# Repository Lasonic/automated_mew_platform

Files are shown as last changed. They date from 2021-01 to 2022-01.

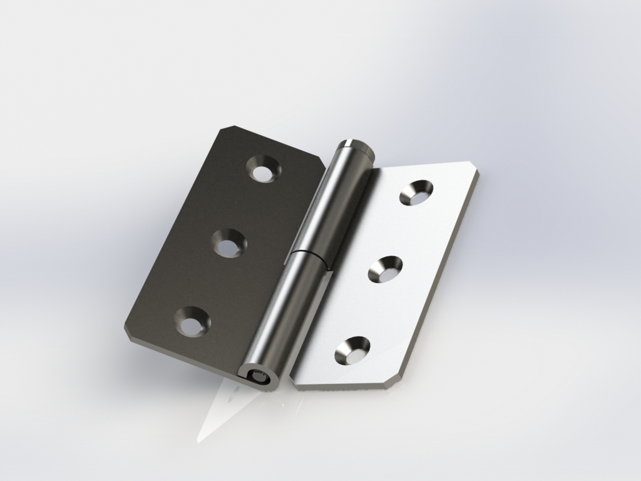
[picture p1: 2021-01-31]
CAD/Hinges/prt.JPG

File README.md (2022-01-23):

# automated_mew_platform
Files including all python, arduino and matlab code necessary to run the platform.  

Repository withe design files and code for Automated MEW platform with real-time process monitoring.

Publication avalilabe at :https://www.sciencedirect.com/science/article/pii/S2468067221000766

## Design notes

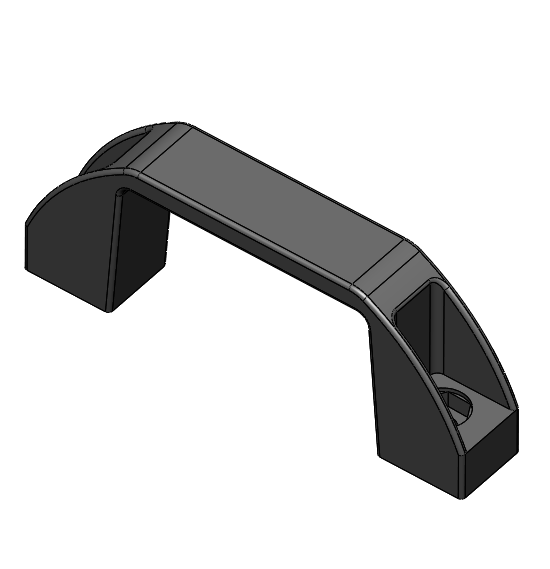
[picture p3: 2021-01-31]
CAD/Handle/Capture.PNG

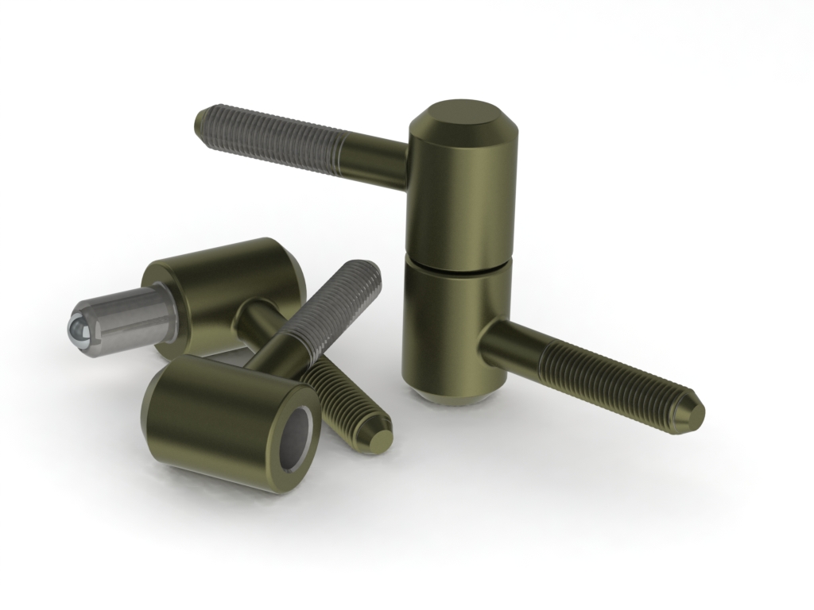
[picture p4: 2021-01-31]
CAD/Hinges/trt3.JPG

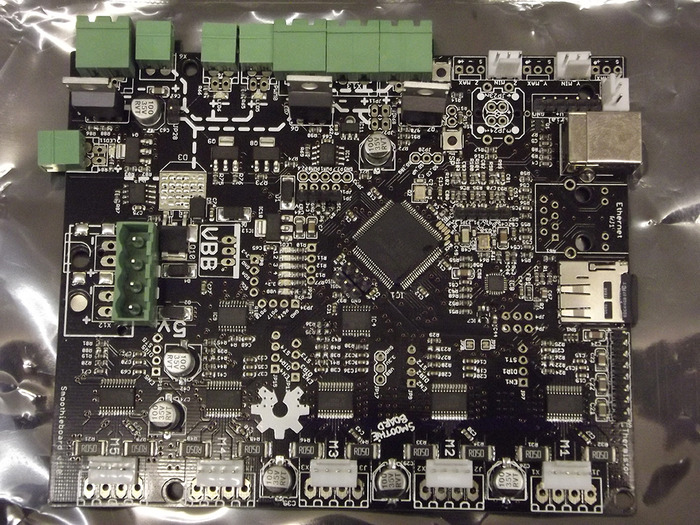
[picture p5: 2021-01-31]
CAD/Smoothie board/Renderings/4c55661e1bbb966e016c8f90354837cf_large.jpg

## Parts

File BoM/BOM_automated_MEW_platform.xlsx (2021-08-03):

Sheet: Mechanical
Componenet | Source | Catalog number | Quantity | Cost/Unit (USD) | Total cost (USD) | Qty | Part Name | Part Link | Comments
Framework |  |  |  |  |  | 1 | OpenBuilds MiniMill | http://openbuildspartstore.com/openbuilds-minimill/ | Convenient One Click Bundle
Profile 30 x 30 mm (slot 8 mm) | GAP Engineering Pty Ltd (Australia) | 084.107.002 needs cutting | 19.464 | 11.04 | 214.88 | 8 | 8mm Shim | http://openbuildspartstore.com/8mm-shim/ | SKU 835
Profile 20 x 20 mm (slot 6 mm) | GAP Engineering Pty Ltd (Australia) | 084.111.001 needs cutting | 2.21 | 7.71 | 17.04 | 6 | 90 Degree Joining Plate | http://openbuildspartstore.com/90-degree-joining-plate/ | SKU 610
Profile 20 x80 mm (V slot) | Makerstore(Australia) | LR-2080-S needs cutting | 2 | 22.82 | 45.64 | 6 | Aluminum Spacers - 3mm | http://openbuildspartstore.com/aluminum-spacers/ | SKU 175
Clamping angle 29x29mm | GAP Engineering Pty Ltd (Australia) | 084.305.010 | 50 | 2.16 | 108.00 | 6 | Aluminum Spacers - 40mm | http://openbuildspartstore.com/aluminum-spacers/ | SKU 95
Clamping angle 18x18mm | GAP Engineering Pty Ltd (Australia) | 084.305.032 | 40 | 1.66 | 66.40 | 8 | Aluminum Spacers - 6mm | http://openbuildspartstore.com/aluminum-spacers/ | SKU 90
Hammer Nut M5 slot 8 | GAP Engineering Pty Ltd (Australia) | 084.302.023 pack of 5 | 20 | 3.08 | 61.60 | 3 | Anti-Backlash Nut Block | http://openbuildspartstore.com/anti-backlash-nut-block-fo... | SKU 1055
Hammer Nut M5 slot 6 | GAP Engineering Pty Ltd (Australia) | 084.302.061 pack of 5 | 20 | 3.08 | 61.60 | 6 | Ball Bearing 688Z 8x16x5 | http://openbuildspartstore.com/ball-bearing-688z-8x16x5/ | SKU 780
Nut M5 | GAP Engineering Pty Ltd (Australia) | 084.302.002 pack of 25 | 2 | 3.85 | 7.70
Nut M8 | GAP Engineering Pty Ltd (Australia) | 084.302.002 pack of 25 | 2 | 3.85 | 7.70 | 6 | Black Angle Corner Connector | http://openbuildspartstore.com/black-angle-corner-connector/ | SKU 540
Stainless steel plain washer M5 | RS componenets (Australia) | 527-397 | 1 | 9.84 | 9.84 | 10 | Cable Ties | http://openbuildspartstore.com/cable-ties-10-pack/ | SKU 675 - Sold in Packs - Need 10 Singles
Screw M8x20 | GAP Engineering Pty Ltd (Australia) | 084.301.003 pack of 25 | 2 | 4.62 | 9.24 | 10 | Cast Corner Bracket | http://openbuildspartstore.com/cast-corner-bracket/ | SKU 490
Screw M5x20 | GAP Engineering Pty Ltd (Australia) | 084.301.036 pack of 25 | 2 | 2.89 | 5.78 | 5 | C-Beam® Linear Rail | http://openbuildspartstore.com/c-beam-linear-rail/ | (1) 107mm (3) 250mm (1) 390mm
Low profile M5x15 | Makerstore(Australia) | SCREWS-M5-LP-15/10 pack of 10 | 10 | 1.38 | 13.80
Door handle | GAP Engineering Pty Ltd (Australia) | 084.504.002 | 3 | 3.39 | 10.17 | 1 | C-Beam® Gantry Plate - Double Wide | http://openbuildspartstore.com/c-beam-gantry-plate-double... | SKU 2026
Aluminium hinge | GAP Engineering Pty Ltd (Australia) | 084.500.003 | 6 | 11.93 | 71.58 | 6 | C-Beam® End Mount | http://openbuildspartstore.com/c-beam-end-mount/ | SKU 965
Alumimium sheet 770x290x3mm | Action Alumimium (Australia) | N/A | 1 | 15.26 | 15.26
Enclosure
Acrylic sheet, 4.5mm, matt black | Mulford Plastics Pty Ltd (Australia) | ACB4.5_11440 | 3 | 125.38 | 376.14
Low profile M5x15 | Makerstore(Australia) |  |  |  | 0.00
Hammer Nut M5 slot 8 | GAP Engineering Pty Ltd (Australia) |  |  |  | 0.00
Printhead |  |  |  |  |  | 8 | Eccentric Spacer - 6mm | http://openbuildspartstore.com/eccentric-spacer/ | SKU 226
Teflon main body | Eastagate engineering (Australia) | Quotation based on the provided drawings | 1 | 85.55 | 85.55
Teflon cap | Eastagate engineering (Australia) | Quotation based on the provided drawings | 1 | 36.22 | 36.22
Teflon small insert | Eastagate engineering (Australia) | Quotation based on the provided drawings | 1 | 15.1 | 15.10
Brass insert | Eastagate engineering (Australia) | Quotation based on the provided drawings | 1 | 63.6 | 63.60
 |  |  |  |  | 0.00
Linear stages |  |  |  |  |  | 2 | V-Slot® Door Handle | http://openbuildspartstore.com/v-slot-door-handle/ | SKU 556
OpenBuilds MiniMill CNC Machine | Openbuilds(USA) | 2170-Bundle | 1 | 549.99 | 549.99 | 2 | Jog Knob | http://openbuildspartstore.com/jog-knob/ | SKU 2040
This includes:
8mm Shim | Openbuilds(USA) | SKU 835 | 8 |  |  | 1 | L Bracket - Single | http://openbuildspartstore.com/l-bracket/ | SKU 545
90 Degree Joining Plate | Openbuilds(USA) | SKU 610 | 6 |  |  | 3 | Lead Screw | http://openbuildspartstore.com/8mm-metric-acme-lead-screw/ | (1) 290mm (1) 315mm (1) 455mm
Aluminum Spacers - 3mm | Openbuilds(USA) | SKU 175 | 6 |  |  | 6 | Lock Collar - 8mm | http://openbuildspartstore.com/lock-collar/ | SKU 840
Aluminum Spacers - 40mm | Openbuilds(USA) | SKU 95 | 6 |  |  | 48 | Low Profile Screws M5 - 10mm | http://openbuildspartstore.com/low-profile-screws-m5/ | SKU 878 - Sold in Packs - Need 42 Singles
Aluminum Spacers - 6mm | Openbuilds(USA) | SKU 90 | 8 |  |  | 8 | Low Profile Screws M5 - 12mm | http://openbuildspartstore.com/low-profile-screws-m5/ | SKU 2190 - Sold in Packs - Need 8 Singles
Anti-Backlash Nut Block | Openbuilds(USA) | SKU 1055 | 3 |  |  | 30 | Low Profile Screws M5 - 20mm | http://openbuildspartstore.com/low-profile-screws-m5/ | SKU 750 - Sold in Packs - Need 30 Singles
Ball Bearing 688Z 8x16x5 | Openbuilds(USA) | SKU 780 | 6 |  |  | 8 | Low Profile Screws M5 - 25mm | http://openbuildspartstore.com/low-profile-screws-m5/ | SKU 20 - Sold in Packs - Need 8 Singles
Black Angle Corner Connector | Openbuilds(USA) | SKU 540 | 6 |  |  | 6 | Low Profile Screws M5 - 55mm | http://openbuildspartstore.com/low-profile-screws-m5/ | SKU 760 - Sold in Packs - Need 6 Singles
Cable Ties | Openbuilds(USA) | SKU 675 - Sold in Packs - Need 10 Singles | 10 |  |  | 21 | Low Profile Screws M5 - 8mm | http://openbuildspartstore.com/low-profile-screws-m5/ | SKU 946 - Sold in Packs - Need 21 Singles
Cast Corner Bracket | Openbuilds(USA) | SKU 490 | 10 |  |  | 8 | Xtreme Mini V Wheel™ Kit | http://openbuildspartstore.com/xtreme-mini-v-wheel-kit/ | SKU 876
C-Beam® Linear Rail | Openbuilds(USA) | (1) 107mm (3) 250mm (1) 390mm | 5 |  |  | 4 | Precision Shim - 10x5x1mm | http://openbuildspartstore.com/precision-shim-10x5x1mm/ | SKU 05
C-Beam® Gantry Plate - Double Wide | Openbuilds(USA) | SKU 2026 | 1 |  |  | 1 | Router/Spindle Mount | http://openbuildspartstore.com/router-spindle-mount/ | SKU 990
C-Beam® End Mount | Openbuilds(USA) | SKU 965 | 6 |  |  | 10 | Self Tapping Screw | http://openbuildspartstore.com/self-tapping-screw/ | SKU 720
C-Beam® Gantry Plate - XLarge | Openbuilds(USA) | SKU 2030 | 2 |  |  | 60 | Tee Nuts - M5 | http://openbuildspartstore.com/tee-nuts-25-pack/ | SKU 536 - Sold in Packs - Need 60 Singles
Drop In Tee Nuts | Openbuilds(USA) | SKU 230 | 4 |  |  | 8 | Xtreme Solid V Wheel™ Kit | http://openbuildspartstore.com/xtreme-solid-v-wheel-kit/ | SKU 465
Eccentric Spacer - 6mm | Openbuilds(USA) | SKU 226 | 8 |  |  | 4 | 3 Hole Joining Strip Plate | http://openbuildspartstore.com/3-hole-joining-strip-plate/ | SKU 646
1/4" x 8mm Flexible Coupling | Openbuilds(USA) | SKU 155 | 3 |  |  | 8 | Low Profile Screws M5 - 27mm | https://openbuildspartstore.com/low-profile-screws-m5-10-... | SKU 2260 - Sold in Packs - Need 8 Singles
V-Slot® Door Handle | Openbuilds(USA) | SKU 556 | 2 |  |  | 1 | Ball Driver Screw Driver Set | https://openbuildspartstore.com/balldriver-screw-driver-set/ | SKU 2145
Jog Knob | Openbuilds(USA) | SKU 2040 | 2 |  |  | 4 | Nylon Insert Hex Locknut M5 - Black | https://openbuildspartstore.com/nylon-insert-hex-locknut-... | SKU 2285
L Bracket - Single | Openbuilds(USA) | SKU 545 | 1 |  |  | 1 | OpenBuilds 8mm Spanner Wrench | https://openbuildspartstore.com/openbuilds-8mm-spanner-wr... | SKU 2265
Lead Screw | Openbuilds(USA) | (1) 290mm (1) 315mm (1) 455mm | 3 |  |  | 6 | Round Head Cutting Screws | https://openbuildspartstore.com/round-head-cutting-screws... | SKU 2440
Lock Collar - 8mm | Openbuilds(USA) | SKU 840 | 6 |  |  | 1 | Spindle/Router LED Light Ring | https://openbuildspartstore.com/spindle-router-led-light-... | SKU 2225
Low Profile Screws M5 - 10mm | Openbuilds(USA) | SKU 878 - Sold in Packs - Need 42 Singles | 48 |  |  | 1 | Xtension Wire 2C - 3' | https://openbuildspartstore.com/xtension-wire-by-the-foot/ | SKU 2545-By-the-Foot
Low Profile Screws M5 - 12mm | Openbuilds(USA) | SKU 2190 - Sold in Packs - Need 8 Singles | 8 |  |  | 3 | Xtension Wire 4C - 3' | https://openbuildspartstore.com/xtension-wire-by-the-foot/ | SKU 2556
Low Profile Screws M5 - 20mm | Openbuilds(USA) | SKU 750 - Sold in Packs - Need 30 Singles | 30 |  |  | 1 | Rubber Feet Set | https://openbuildspartstore.com/rubber-feet-set-4-pack/ | SKU 2645-Set
Low Profile Screws M5 - 25mm | Openbuilds(USA) | SKU 20 - Sold in Packs - Need 8 Singles | 8 |  |  | 1 | Flexible Tubing - 1' | https://openbuildspartstore.com/flexible-corrugated-tubing/ | SKU 2675-By-the-Foot
Low Profile Screws M5 - 55mm | Openbuilds(USA) | SKU 760 - Sold in Packs - Need 6 Singles | 6 |  |  | 1 | Flexible Tubing - 1.5' | https://openbuildspartstore.com/flexible-corrugated-tubing/ | SKU 2675-By-the-Foot
Low Profile Screws M5 - 8mm | Openbuilds(USA) | SKU 946 - Sold in Packs - Need 21 Singles | 21 |  |  | 4 | Flexible Tubing Clamps | https://openbuildspartstore.com/flexible-tubing-clamps/ | SKU 2685
Xtreme Mini V Wheel™ Kit | Openbuilds(USA) | SKU 876 | 8 |  |  | 3 | Xtension Limit Switch Kit | https://openbuildspartstore.com/xtension-limit-switch-kit/ | SKU 2805
Precision Shim - 10x5x1mm | Openbuilds(USA) | SKU 05 | 4 |  |  | 3 | Xtension Wire 3C - 3' | https://openbuildspartstore.com/xtension-wire-by-the-foot/ | SKU 2905
Router/Spindle Mount | Openbuilds(USA) | SKU 990 | 1 |  |  | 2 | Slot Cover/Panel Holder - 250mm - Black | https://openbuildspartstore.com/slot-cover-panel-holder/ | SKU 125-LP-B
Self Tapping Screw | Openbuilds(USA) | SKU 720 | 10 |  |  | 4 | NEMA 23 Stepper Motor | https://openbuildspartstore.com/nema-23-stepper-motor/ | SKU 518 - Option to Include With Bundle
Tee Nuts - M5 | Openbuilds(USA) | SKU 536 - Sold in Packs - Need 60 Singles | 60 |  |  | 1 | 24V Meanwell Power Supply Bundle | https://openbuildspartstore.com/24v-meanwell-power-supply... | SKU 591 - Option to Include With Bundle
Xtreme Solid V Wheel™ Kit | Openbuilds(USA) | SKU 465 | 8 |  |  | 1 | Dust Shoe | https://openbuildspartstore.com/dust-shoe/ | SKU 2795 - Option to Include With Bundle
3 Hole Joining Strip Plate | Openbuilds(USA) | SKU 646 | 4 |  |  | 1 | BlackBox Motion Control System | https://openbuildspartstore.com/blackbox-motion-control-s... | SKU 2790 - Option to Include With Bundle
Low Profile Screws M5 - 27mm | Openbuilds(USA) | SKU 2260 - Sold in Packs - Need 8 Singles | 8 |  |  | 1 | DeWALT DWP611 Compact Router | https://openbuildspartstore.com/dewalt-dwp611-compact-rou... | SKU 2390 - Option to Include With Bundle
Ball Driver Screw Driver Set | Openbuilds(USA) | SKU 2145 | 1 |  |  | 1 | VCarve Desktop | https://openbuildspartstore.com/vcarve-desktop/ | SKU 2885 - Option to Include With Bundle
Nylon Insert Hex Locknut M5 - Black | Openbuilds(USA) | SKU 2285 | 4 |  |  | 0
OpenBuilds 8mm Spanner Wrench | Openbuilds(USA) | SKU 2265 | 1
Round Head Cutting Screws | Openbuilds(USA) | SKU 2440 | 6
Spindle/Router LED Light Ring | Openbuilds(USA) | SKU 2225 | 1
Xtension Wire 2C - 3' | Openbuilds(USA) | SKU 2545-By-the-Foot | 1
Xtension Wire 4C - 3' | Openbuilds(USA) | SKU 2556 | 3
Rubber Feet Set | Openbuilds(USA) | SKU 2645-Set | 1
Flexible Tubing - 1' | Openbuilds(USA) | SKU 2675-By-the-Foot | 1
Flexible Tubing - 1.5' | Openbuilds(USA) | SKU 2675-By-the-Foot | 1
Flexible Tubing Clamps | Openbuilds(USA) | SKU 2685 | 4
Xtension Limit Switch Kit | Openbuilds(USA) | SKU 2805 | 3
Xtension Wire 3C - 3' | Openbuilds(USA) | SKU 2905 | 3
Slot Cover/Panel Holder - 250mm - Black | Openbuilds(USA) | SKU 125-LP-B | 2
Printbed
Aluminium plate 120x120x10mm | Action Alumimium (Australia) | N/A | 1 | 7.7 | 7.70
Low Profile Screws M5 - ? | Makerstore(Australia) |  |  |  | 0.00
 |  |  |  |  | 1860.53

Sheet: Electrical
Component | Source | Catalog number | Quantity | Cost/Unit (USD) | Total cost (USD)
Embedded control unit
Smoothieboard 5XC v1.1 | Uberlock (USA) | smoothie_5x | 1 | 188.97 | 188.97
Arduino Due | RS Components (Australia) | 769-7412 | 1 | 40.76 | 40.76
USB to TTL Serial Cable | Core Electronics(Australia) | ADA954 | 2 | 17.18 | 34.36
PCB components
PCB manufacture | JLCPCB | N/A | 1 | 7.41 | 7.41
Resistor network 10K/10K | Mouser electronics | 71-MPM2002AT1 | 2 | 4.74 | 9.48
Resistor network 10K/5K | Mouser electronics | 71-MPMA50011002AT5 | 2 | 4.48 | 8.96
Capacitor ceramic 100V 0.10uF 5% | Mouser electronics | 810-FA26C0G2A104JRU6 | 5 | 1.18 | 5.9
Capacitor Aluminium Electrolytic Radial 800V 100uF | Mouser electronics | 667-EEU-FS1K101L | 2 | 0.81 | 1.62
Operational Amplifier - TLV2371IDR | Mouser electronics | 595-TLV2371IDR | 2 | 1.34 | 2.68
Computing unit
Desktop PC | Dell (Australia) | N/A | 1 | 1148 | 1148
This includes:
RAM: 64GB
CPU: Intel Xeon, W-2125
Operating system: Windows 10, 64-bit
Motion control
Integrated Stepper Servo Motor Nema 23 Closed Loop | Steppernoline (China) | ISS23-10 | 3 | 94.09 | 282.27
Rigid Coupling 8mm-8mm | Steppernoline (China) | ST-RC07 | 3 | 3.03 | 9.09
Process monitoring
Basker Ace ac2440-75um USB3 Mono | Edmund Optics (USA) | #35-927 | 1 | 1542.95 | 1542.95
1.0X 2/3" GoldTL™ Telecentric Lens | Edmund Optics (USA) | #55-350 | 1 | 1667.21 | 1667.21
USB3.1 Locking Cable, 5m | Edmund Optics (USA) | #88-058 | 1 | 40 | 40
Mounting Clamp, 68mm Inner Diameter | Edmund Optics (USA) | #56-024 | 1 | 153.16 | 153.16
Temperature control
Heating element - syringe | Rauschert (Germany) |  | 1 | 192.73 | 192.73
Heating element - ring | Rauschert (Germany) |  |  |  | 0
RS PRO K-type thermocouple | RS Components (Australia) | 804-7915 | 2 | 32.95 | 65.9
RS PRO ANSI thermocouple connector male | RS Components (Australia) | 769-1101 | 2 | 7.53 | 15.06
RS PRO ANSI thermocouple connector female | RS Components (Australia) | 769-1173 | 2 | 3.23 | 6.46
K-type thermocouple wire extension | RS Components (Australia) | 200-0623 - length 25m - need 5m | 0.25 | 39.62 | 9.905
Analog Output K-Type Thermocouple Amplifier | Core Electronics(Australia) | ADA1778 | 2 | 20.81 | 41.62
High voltage
High voltage supply | Gamma High Voltage | RC5-20P/24 | 1 | 557 | 557
High voltage connector |  |  |  |  | 0
Pneumatic pressure system
SMC pressure regulator (ITV1050-31N2L) | SMC Pneumatics (USA) | ITV1050-31N2L | 1 | 294.2 | 294.2
Schmaltz pressure sensor including connecting cable | Schmalz Australia (Australia) | 10.06.02.00561 | 1 | 150 | 150
Input connector |  |  |  |  | 0
output connector |  |  |  |  | 0
Input hose |  |  |  |  | 0
Output hose |  |  |  |  | 0
T junction |  |  |  |  | 0
Power unit
320W 48VDC switching power supply (RSP-320-48) | Mouser electronics | 709-RSP320-48 | 1 | 57.88 | 57.88
350W 12VDC switching power supply (LRS-350-12) | Mouser electronics | 709-LRS350-12 | 1 | 38.28 | 38.28
68W 5VDC & 24VDC dual output switching power supply (RD-65B) | Mouser electronics | 709-RD65B | 1 | 23.49 | 23.49
IEC panel mount connector male | RS Components (Australia) | 352-1803 | 1 | 14.86 | 14.86
2m power cable, IEC to AS/NZS 3112 | RS Components (Australia) | 909-2178 | 1 | 13.01 | 13.01
Flexible 3-core mains cable | Jaycar Electronics (Australia) | WB1562 - sold per meter | 2 | 2.19 | 4.38
DIN rail | RS Components | 467-406 | 1 | 7.63 | 7.63
DIN rail grey terminal | Altronics (Australia) | P2400 | 26 | 2.23 | 57.98
DIN rail green/yellow terminal | Altronics (Australia) | P2412 | 4 | 4.43 | 17.72
Omron 24VDC coil non-latching relay SPDT, 10A | RS Components (Australia) | 329-7178 | 1 | 11.41 | 11.41
DIN rail Omron 5 Pin Relay Socket | RS Components (Australia) | 111-3066 | 1 | 7.58 | 7.58
Black Shorting Link for DIN rail terminals | Altronics (Australia) | P2469 | 2 | 2.87 | 5.74
Red Shorting Link for DIN rail terminals | Altronics (Australia) | P2463 | 2 | 2.87 | 5.74
Safety hardware
Contactless magnetic switch | Element14 (USA) | 2847408 | 2 | 388.26 | 776.52
Wire and connectors
Female Crimp Pins for 0.1" Housings | Core Electronics(Australia) | POLOLU-1930 - pack of 100 | 1 | 6.63 | 6.63
0.1" Crimp Connector Housing: 1x1 | Core Electronics(Australia) | POLOLU-1900 - pack of 25 | 1 | 1.38 | 1.38
0.1" Crimp Connector Housing: 1x4 | Core Electronics(Australia) | POLOLU-1903 - pack of 10 | 1 | 1.38 | 1.38
Power cable 0.5mm^2- RED |  |  |  |  | 0
Power cable 0.5mm^2 - BLACK |  |  |  |  | 0
4 core cable, 0.5mm2, screened | Element14 (USA) | PP001563 - sold per 50 m | 0.2 | 78.39 | 15.68
2 core cable, 0.5mm2, screened | Element14 (USA) | PP001555 - sold per 50m | 0.2 | 50.47 | 10.09
Jumper cable male-female | Core Electronics(Australia) | FIT0365 | 1 | 5.46 | 5.46
Jumper cable male-male | Core Electronics(Australia) | POLOLU-1702 - pack of 50 | 1 | 13.9 | 13.9
Jumper cable female-female | Core Electronics (Australia) | 018-03-DUPONT-PK | 1 | 7.62 | 7.62
Heat shrink kit | Core Electronics (Australia) | PRT-09353 | 1 | 9.13 | 9.13
Drag chain | Makerstore (Australia) | BUN-CDCL | 1 | 65.41 | 65.41
Breadboard | Core Electronics (Australia) | CE00304 | 1 | 5.06 | 5.06
40 Pin Headers | Core Electronics (Australia) | FIT0084 - pack of 10 | 1 | 3.15 | 3.15
 |  |  |  |  | 7662.807

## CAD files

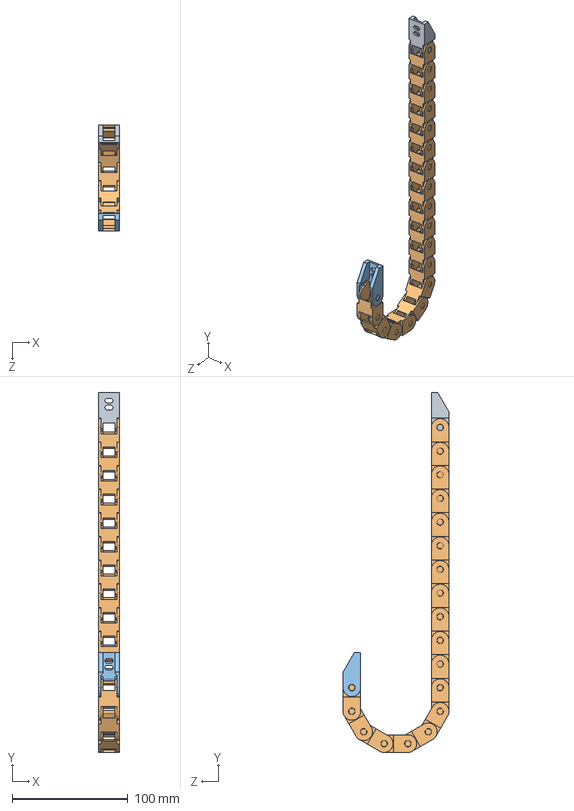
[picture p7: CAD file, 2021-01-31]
CAD/Drag chain/Drag Chain 10x10.SLDASM
17.8 x 310.8 x 91.5 mm
Bloc 06.stp
Bloc 04.stp x 18
Bloc 05.stp

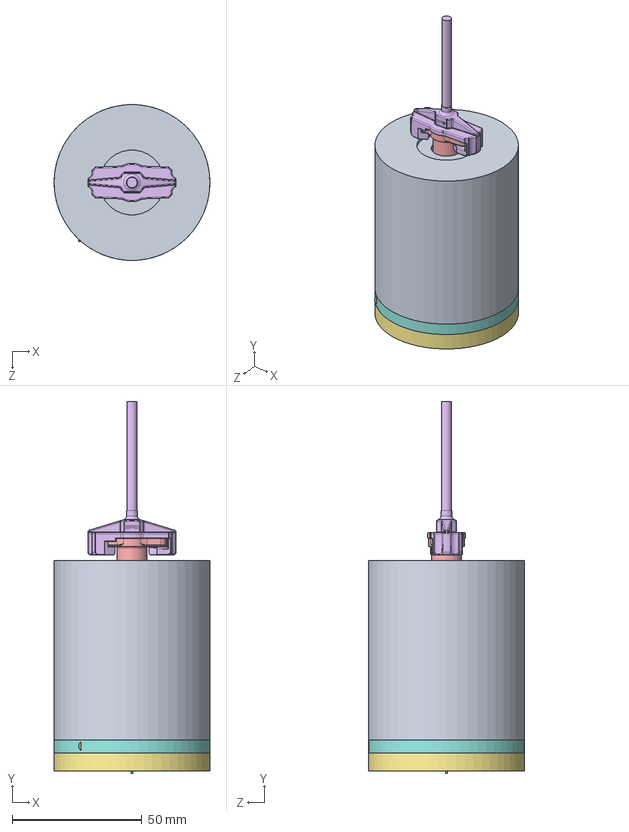
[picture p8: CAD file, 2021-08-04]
CAD/Printhead/Printhead CAD/head_1111.SLDASM
60.0 x 143.2 x 60.0 mm
Ceramic heater_CSIRO
heater_bottom_CSIRO
23GP_final
NORDSONEFD-7012030 PISTON O 3CC WH WIPER
NORDSONEFD-7012013 BARREL O 3CC CL
PumpConnection_CSIRO
ring_bottom
ring_middle
TUBE_TOP
brass

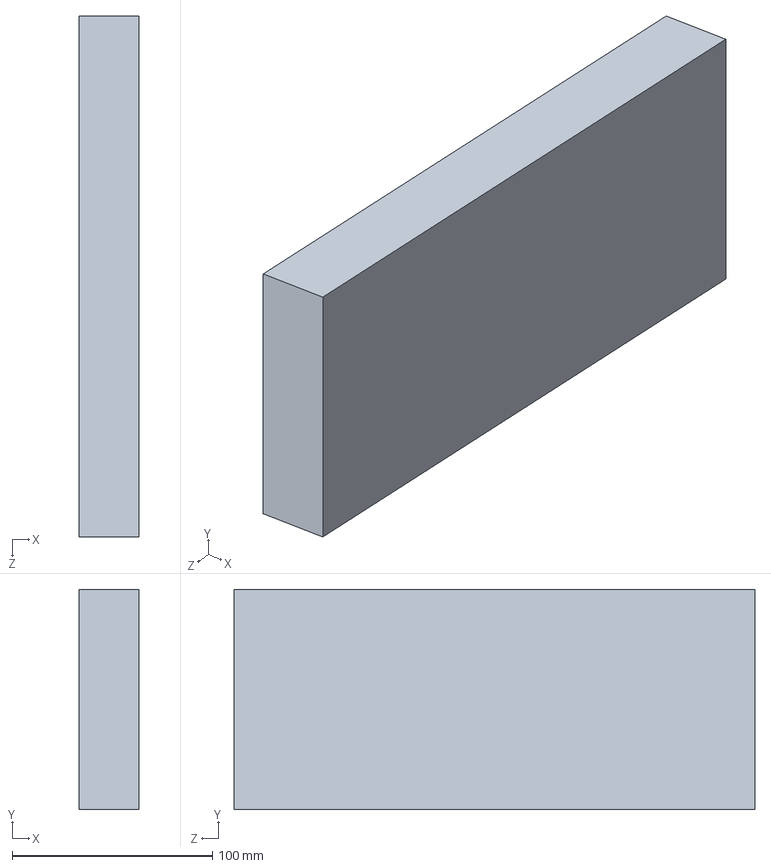
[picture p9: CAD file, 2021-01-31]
CAD/Electrical components/24VDC PSU + mains adapter.SLDPRT
30.0 x 110.0 x 260.0 mm

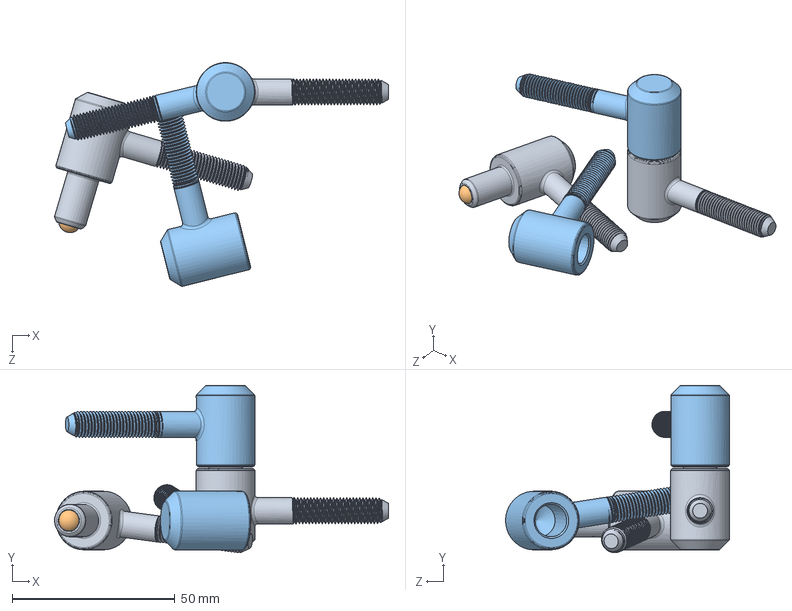
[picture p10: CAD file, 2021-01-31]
CAD/Hinges/Sarka za vrata.SLDASM
102.5 x 51.4 x 68.7 mm
telo 2 x 2
topce x 2
telo x 2

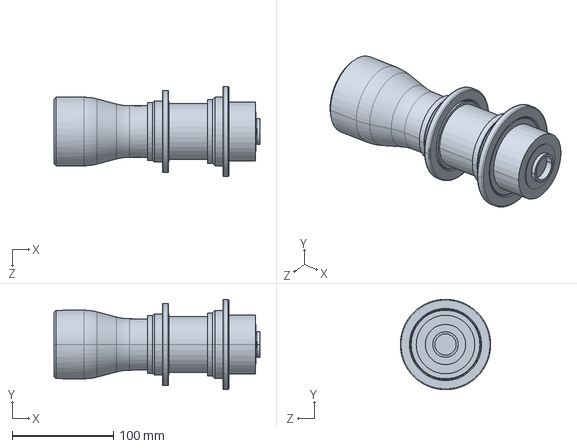
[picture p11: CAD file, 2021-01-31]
CAD/Lens.SLDASM
203.8 x 89.5 x 89.5 mm

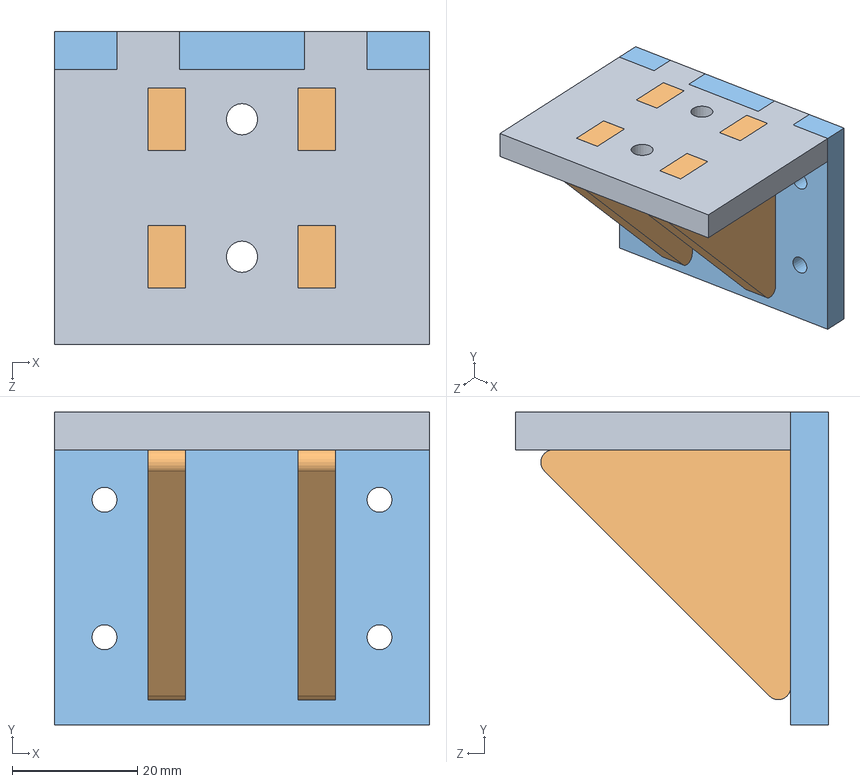
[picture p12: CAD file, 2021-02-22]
CAD/Pressure regulator bracket/Pressure support bracket.SLDASM
60.0 x 50.0 x 50.0 mm
Side part
Support corner bracket x 2
Top part

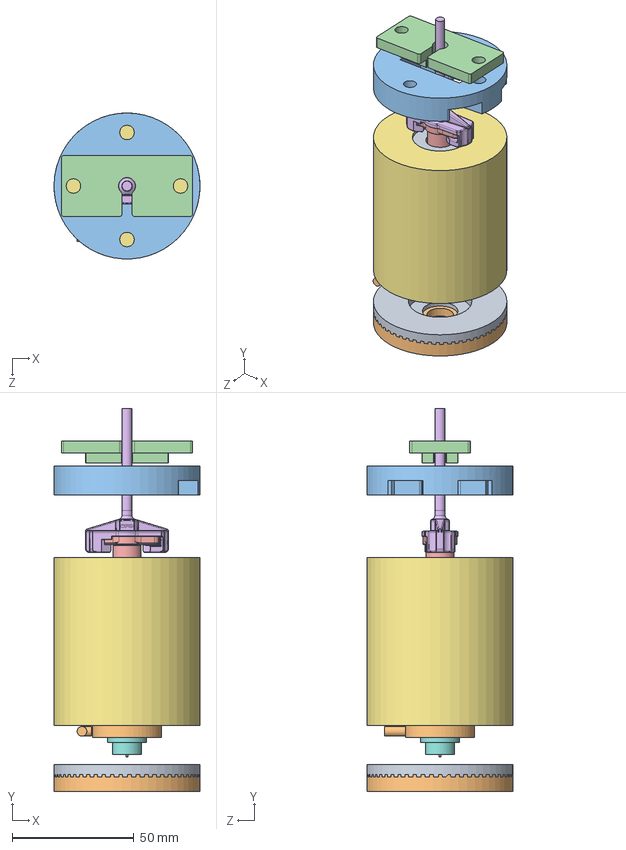
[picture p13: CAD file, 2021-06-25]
CAD/Printhead/Printhead CAD/head_final_assembly.SLDASM
60.0 x 157.4 x 60.0 mm
Ceramic heater_CSIRO
heater_bottom_CSIRO
23GP_final
NORDSONEFD-7012030 PISTON O 3CC WH WIPER
NORDSONEFD-7012013 BARREL O 3CC CL
PumpConnection_CSIRO
TUBE_TOP
brass
ring_middle
ring_bottom
Printhead_top_part
Syringe_top_clamp

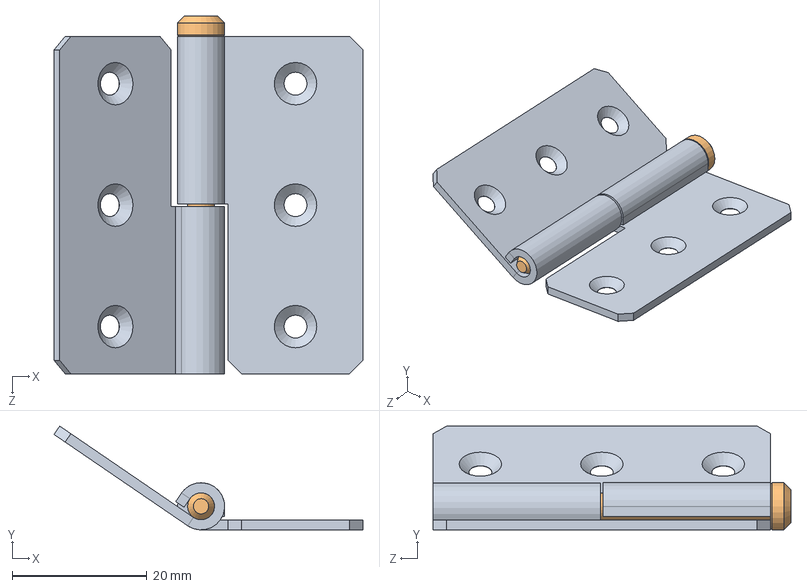
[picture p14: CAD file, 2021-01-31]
CAD/Hinges/Leptir sarka.SLDASM
45.8 x 15.4 x 53.0 mm
krilo 1 x 2
Klin

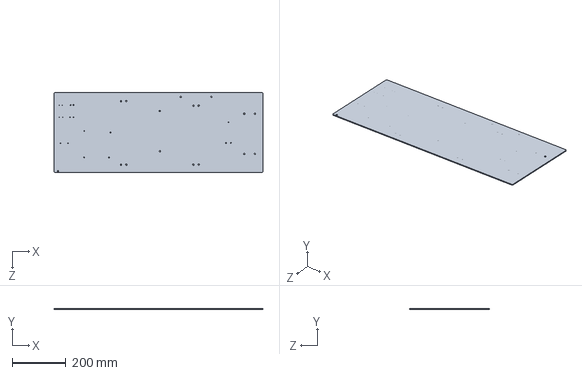
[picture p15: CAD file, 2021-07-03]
CAD/Aluminum_plate_electronics_final.SLDPRT
780.0 x 3.00 x 300.0 mm

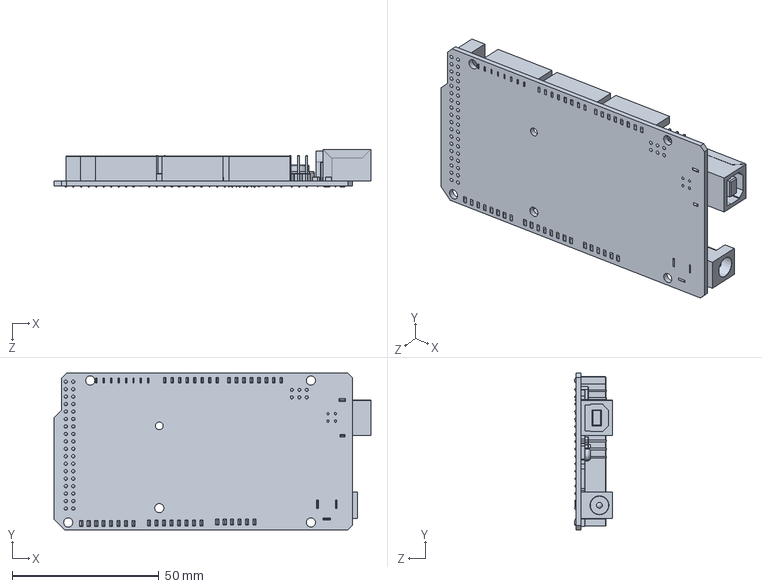
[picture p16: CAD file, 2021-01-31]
CAD/Arduino/ArduinoMega.SLDPRT
107.9 x 53.4 x 13.0 mm

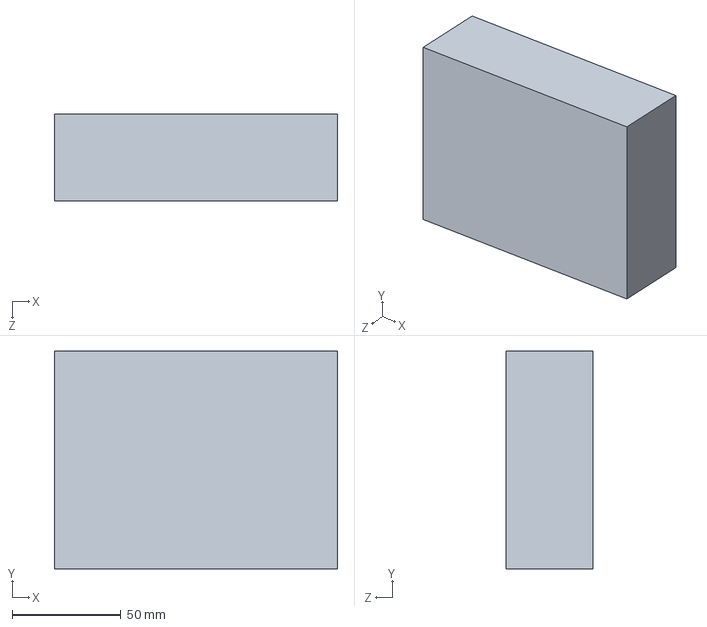
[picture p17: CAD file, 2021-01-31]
CAD/Electrical components/24VDC & 5VDC PSU.SLDPRT
130.0 x 100.0 x 40.0 mm

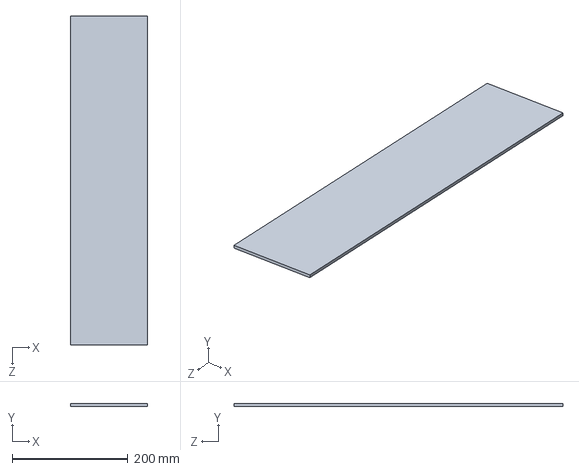
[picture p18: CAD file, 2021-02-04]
CAD/Enclosure/Inner_centre_right_acrylic.SLDPRT
133.1 x 4.50 x 569.0 mm

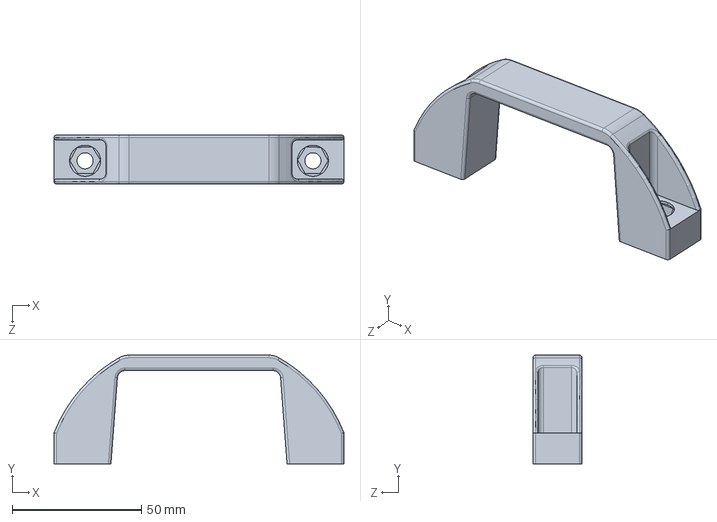
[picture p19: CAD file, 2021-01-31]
CAD/Handle/HANDLE-RTR-DH 19.STEP
112.0 x 42.0 x 19.0 mm

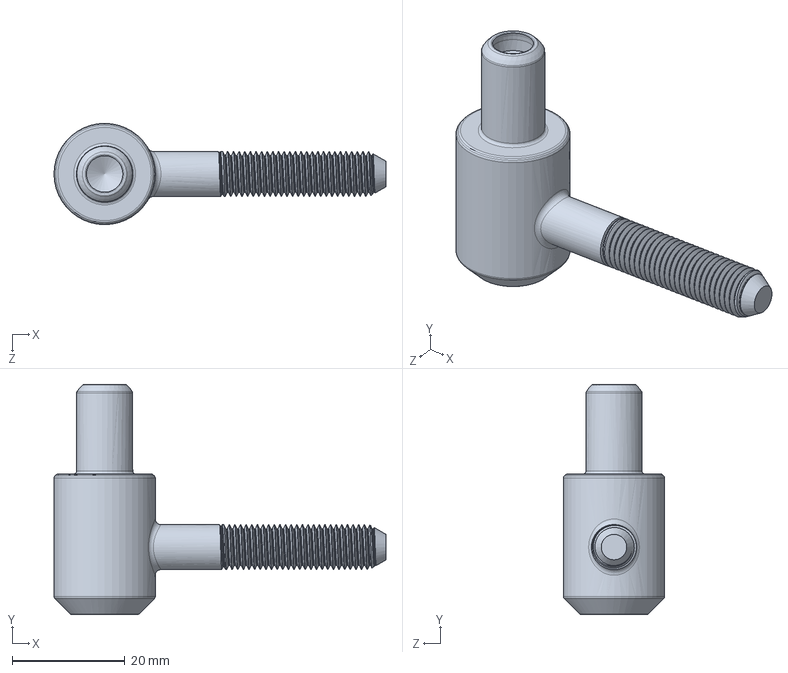
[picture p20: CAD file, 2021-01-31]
CAD/Hinges/telo 2.SLDPRT
59.0 x 40.9 x 18.0 mm

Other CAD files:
CAD/Pressure regulator bracket/Support corner bracket .SLDPRT
CAD/Smoothie board/Smoothieboard_X5.STEP
Firmware_and_software/Arduino_libraries/Adafruit_9DOF/ahrs/processing/cuberotate/data/bunny.obj
CAD/Arduino/ArduinoMega_STEP_AP203.STEP
CAD/Aluminum_plate_electronics.SLDPRT
CAD/Back_bottom_acrylic.SLDPRT
CAD/Back_top_acrylic.SLDPRT
CAD/Bottom_1st_left.SLDPRT
CAD/Door_left.SLDPRT
CAD/Door_right.SLDPRT
CAD/Electrical components/12VDC PSU.SLDPRT
CAD/Electrical components/48VDC PSU.SLDPRT
CAD/Electronics_door.SLDPRT
CAD/Enclosure/Back_bottom_acrylic.SLDPRT
CAD/Enclosure/Back_top_acrylic.SLDPRT
CAD/Enclosure/Bottom_1st_left.SLDPRT
CAD/Enclosure/Door_left.SLDPRT
CAD/Enclosure/Door_right.SLDPRT
CAD/Enclosure/Electronics_door.SLDPRT
CAD/Enclosure/Fron flashing electronic drawer.SLDPRT
CAD/Enclosure/Front_bottom_acrylic.SLDPRT
CAD/Enclosure/Inner_centre_left_acrylic.SLDPRT
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

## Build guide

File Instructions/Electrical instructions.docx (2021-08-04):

Electrical instructions

1. Electrical assembly platform

Timing: 1h

Materials: Aluminium plate, electrical components (power supplies, controller boards, din rail components, cable carrier).

Equipment: Screws, nuts and spacers (M3, M4 and M5), M3 male nylon spacers and nuts, Allen keys.

Critical: Make sure that mechanical components are not in contact with any electrical circuits (especially when assembling small electronic devices).

The aluminium plate of dimensions 770x290x3mm (Figure 1) was used as a base to assemble most of the electrical components of the MEW platform. Figure 2 shows the location of the electrical components on the Aluminium plate. each device was numbered to simplify the assembly.

1) Use M3 screws to mount 12VDC PSU (1), 48VDC PSU (2) and 24/5 VDC PSU (3).
2) Use M4 screws to mount din rail (4).
3) Use M3 Nylon spacers to mount Smoothieboard (5) and create a gap between the device and the asluminium plate.
4) Use M3 screws to mount Arduino Due (6) using a provided plastic base plate.
5) Attach mini breadboard (7) using adhesive.
6) Mount two thermocouple amplifiers (8, 9) and two digital-analog converters (10, 11).
7) Prepare attachment point for five cable carriers (12-16).

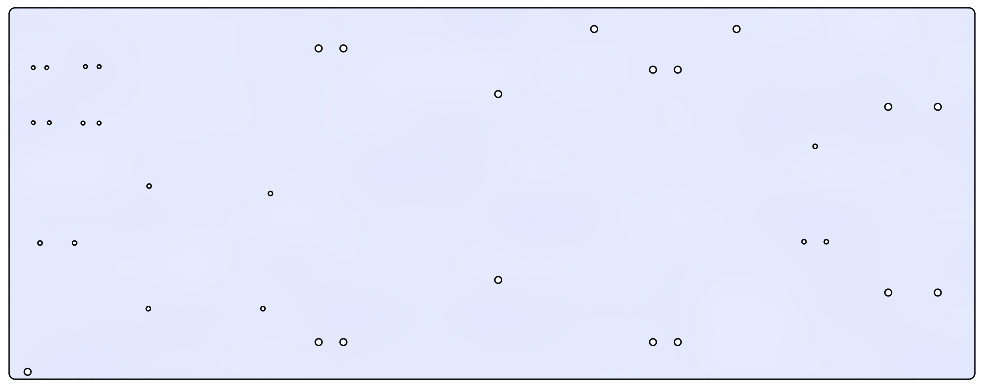
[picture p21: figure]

Figure 1. Aluminium assembly plate ensures quick and straightforward placement of electrical components.

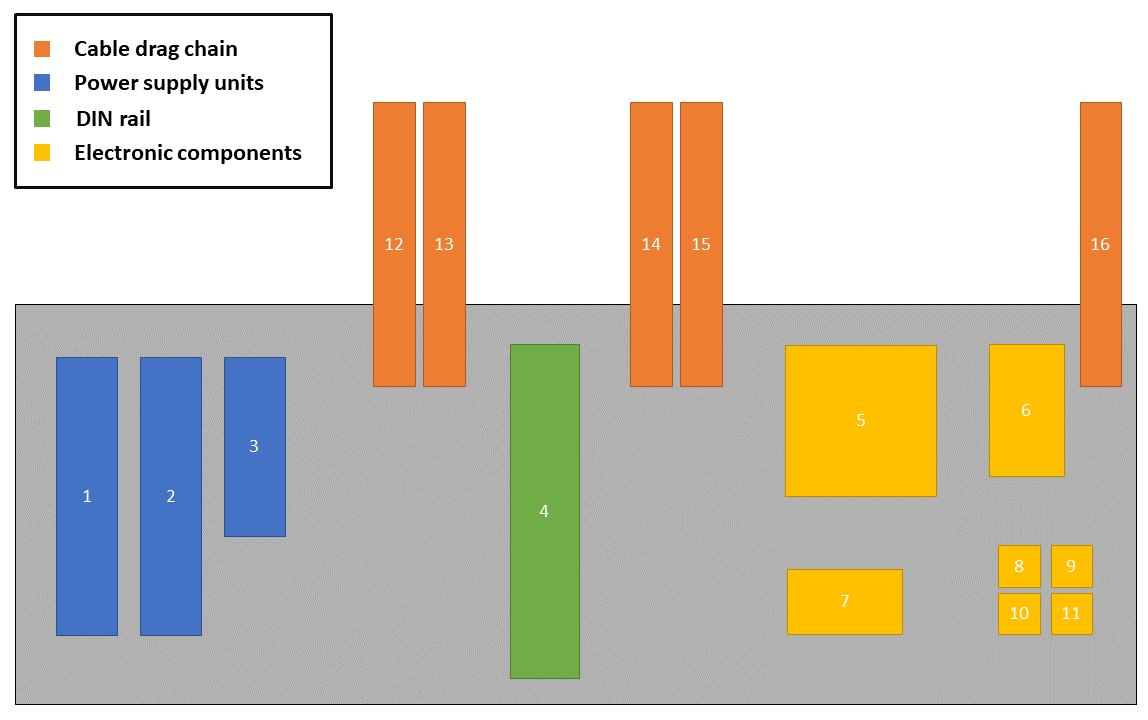
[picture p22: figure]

Figure 2. Distribution of electrical components across the aluminium assembly plate. There are 3 power supplies (blue), 1 din rail (green), 7 electronic components (yellow) and five cable carriers (orange).

2. Cable carriers

Timing: 0.5h

Materials: As listed in the kit documentation.

Equipment: M4, M5 Allen key.

Critical: Test whether the length of each cable carrier is sufficient to allow the drawer to slide out.

A cable carrier was used to provide a neat and convenient way of guiding electrical connections to sensors and actuators. Since the electrical components were mounted on a withdrawable aluminium plate, a cable carrier provided a great solution to maintain a secure and safe connection for moving electrical connections.

The instructions of cable carrier assembly are available online ¹,²

The bottom end of each cable carrier is attached to the aluminium base plate (Figure 3A) while the top end is attached to the aluminium profile (Figure 3B) using L-shaped brackets. Figure 3C shows a final cable carrier assembly.

¹https://www.youtube.com/watch?t=1618&ref=0dnte9dlczx&v=6LY1KcPJ4s4&feature=youtu.be&ab_channel=OpenBuilds (https://www.youtube.com/watch?t=1618&v=6LY1KcPJ4s4&feature=youtu.be&ab_channel=OpenBuilds)

²http://makerhardware.net/wiki/doku.php?id=add_on_packs:cable_drag_chain_mounting_pack

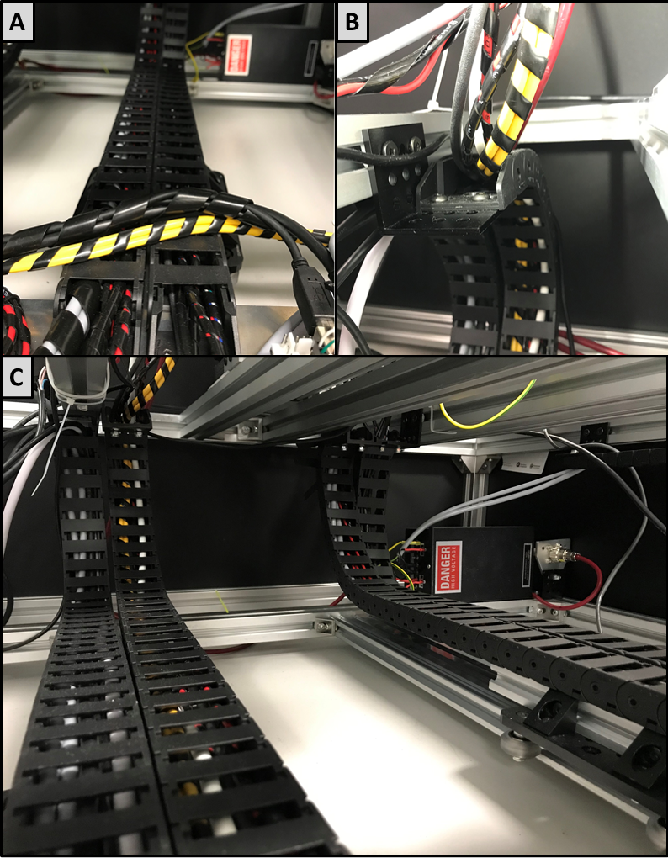
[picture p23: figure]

Figure 3. Cable carrier assembly. A) Bottom end of the cable carrier was assembled staring onto the Aluminium plate. B) Top end of the cable carrier was mounted to an aluminium profile using an L-shaped bracket. C) Assembled cable carriers.

3. Smoothieboard

Timing: 1h

Materials: 1mm² power cables, 0.5mm² 4-core cable, thermocouple, thermocouple extension cable, thermocouple female connector, thermocouple amplifier, XT60 connectors, stepper motors, phoenix connectors (supplied with Smoothieboard), USB type A (male) to USB type B (male) cable.

Equipment: Wire strippers, wire crimping tool.

Critical: Make sure all connections are correctly wired before turning the power on.

The Smoothieboard connection diagram is shown in Figure 4. Refer to this figure during the wiring process.

1) Connect x-axis stepper motor to Smoothieboard. Connect ENA+, DIR+ and PUL+ motor pins to EN1, DIR2, ST1 on Smoothieboard. GND is connected to ENA-, DIR- and PUL-
2) Repeat step 1) for the y-axis and z-axis stepper motors using EN2, DIR2, ST2, EN3, DIR3, ST3. For detailed motor documentation refer to the stepper motor datasheet³.
3) Use dip switches and a lookup table printed each stepper motor to select microstepping to 6400.
4) Connect thermocouple amplifiers⁴.
5) Use a thermocouple extension cable and female a thermocouple connector to connect both syringe and ring thermocouples to the corresponding amplifiers.
6) Connect ring and syringe heaters using XT60 and phoenix connectors.
7) Connect 12VDC PSU.
8) Connect USB-TTL cable via a panel-mount USB connector.
9) Connect Smoothieboard to the PC via a panel-mount USB connector.

³ https://www.omc-stepperonline.com/download/ISS23-10.pdf

⁴ https://www.adafruit.com/product/1778

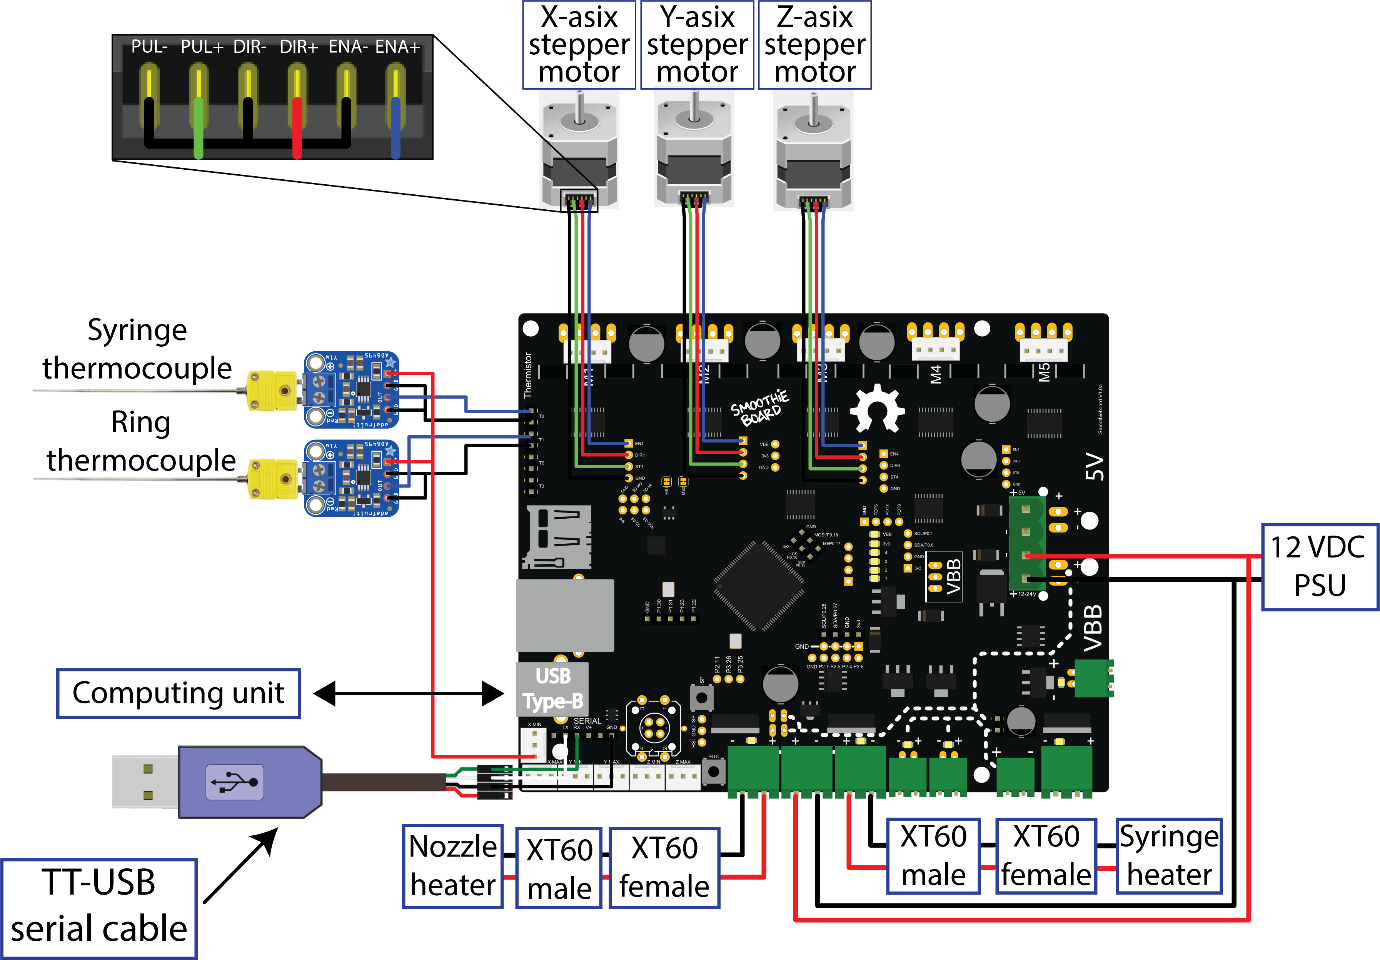
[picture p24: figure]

Figure 4. Simplified Smoothieboard circuit diagram. Three stepper motors, thermocouples, thermocouple amplifiers, nozzle and syringe heaters are connected to Smoothieboard. The computing unit is connected to via USB while the 12VDC power supply provides power to the microcontroller board.

4. Arduino

Timing: 2h

Materials: Jumper cables, USB A to USB micro cable, 1mm² power cables, 0.5mm² 4-core cable, pressure regulator with a connecting cable, pressure sensor with a connecting cable, solder, resistors, operational amplifiers, capacitors, pin headers.

Equipment: Wire strippers, wire crimping tool, soldering iron, tweezers.

Critical: Make sure the connections are made according to the provided circuit diagram. Make sure the VCC and GND connections are properly wired before testing the circuit.

A custom Arduino PCB shield has been designed to allow several sensors and actuators to exchange data. PCB layout and circuit schematic are available in attached documentation⁵. Figure 5 shows a simplified circuit diagram.

Note: The PCB design includes components that are not used in the presented version of the MEW platform and can be considered as a future improvement.

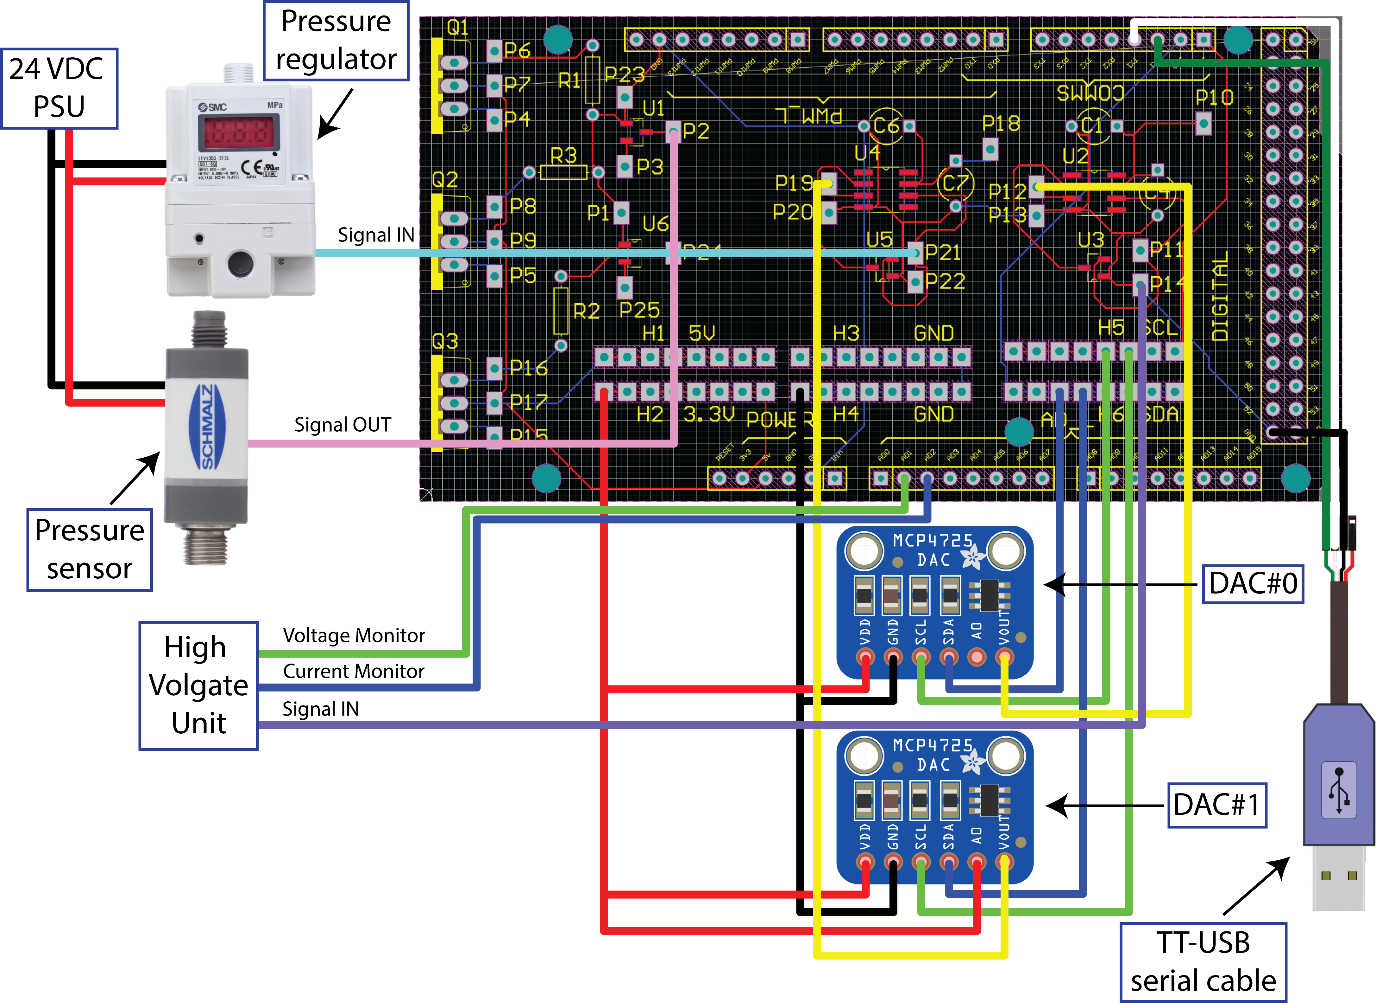
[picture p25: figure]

Figure 5. Simplified Arduino Due and PCB shield circuit diagram. Pressure sensor, pressure regulator, high voltage unit, digital-analog converters are connected to Arduino Due via PCB shield.

⁵https://github.com/Lasonic/automated_mew_platform/tree/master/Electrical%20diagrams/Arduino_shield_PCB

PCB

1) Solder components (R1-3, U1-6, C1-7) as described in the circuit schematic.
2) Solder header pins to POWER, AD_L, DIGITAL, COMMS, PWM_L as shown in.
3) Connect PCB shield to Arduino Due.

Digital-analog converter

Refer to Figure 5 and online tutorial⁶ for wiring instructions of the MCP4725 digital-analog converter.

Pressure sensor

Using provided Schmalz connection cable, connect:

1) Pin 1(Brown) to 24VDC via din terminal.
2) Pin 3(Blue) to GND via din terminal.
3) Pin 4(Black) to P3 on PCB.

Next:

1) Connect P2 to AD0 on PCB.

For more details refer to the pressure sensor datasheet⁷.

Pressure regulator

Using provided SMC connection cable, connect:

1) Pin 1(Brown) to 24VDC.
2) Pin 2(White) to Pin 21 on PCB.
3) Pin 3(Blue) to GND.

Next:

4) Connect P19 to pin VOUT on DAC #1

For more details refer to the pressure regulator datasheet⁸.

High voltage

Using 4-core and earth cable, connect:

1) Pin 1 (earth) to the chassis of the platform.
2) Pin 3 to Pin 11 on PCB.
3) Pin 4 to GND on din terminal.
4) Pin 5 to 24VDC.
5) Pin VM (voltage monitor) to pin AD1.
6) Pin CM (current monitor) to pin AD2.

For more details refer to the High voltage datasheet⁹.

USB connection

1) Connect Arduino to the PC via a panel-mount USB connector.
2) Connect USB-TTL cable via a panel-mount USB connector.

⁶ https://learn.adafruit.com/mcp4725-12-bit-dac-tutorial/wiring

⁷https://github.com/Lasonic/automated_mew_platform/blob/master/Datasheets/schmalz_pressure_sensor_datasheet.pdf

⁸https://github.com/Lasonic/automated_mew_platform/blob/master/Datasheets/SMC_ITV_datasheet.PDF

⁹https://github.com/Lasonic/automated_mew_platform/blob/master/Datasheets/Gamma_high_voltage_datasheet.pdf

5. Din terminals

Timing: 1h

Materials: Aluminium din guide rail, din terminals, relay holder, relay.

Equipment: M5 Allen key, flat head screwdriver.

Critical: Make sure din screw terminals are not shorted with each other (one side of a din screw terminal is exposed and the other one is not).

Figure 6 shows an assembly diagram of DIN screw terminals.

1) Mount Aluminium din rail.
2) Mount grey din terminals (optional: use separator plate between different voltage levels).
3) Use jumpers to distribute the power between terminal blocks.
4) Mount earth terminals and lock them in.
5) Mount a relay holder.
6) Place a relay inside a relay holder.

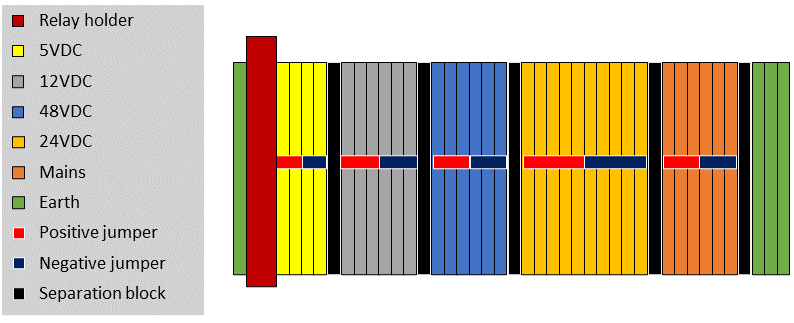
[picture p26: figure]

Figure 6. DIN rail screw terminal assembly diagram. Aluminium din rail and screw terminals are used to supply 5VDC, 12VDC, 24VDC, 48VDC, mains and earth connections of the system. A relay holder provides housing for a 24VDC relay, positive and negative jumpers are used to connect neighbouring terminals, while separation blocks help to keep the design clear and tidy by separating different voltage levels.

6. Power

Timing: 1h

Materials: Power supply units, IEC wall mount connector, mains cable, 1mm² power cables, fork and female spade crimp terminals, earth cable, ring crimp terminal, M5 hammer nut, M5 low profile screw.

Equipment: Crimping tool

Critical: The power system was designed according to Australian standards. Please check and adjust accordingly for other countries.

The power system consists of 3 power supplies: 320W 48VDC, 350W 12VDC, 68W dual output 5 VDC and 24VDC. IEC panel mount connector with a 10A fuse and illuminated switch is used to provide mains power to the platform. Additional earthing connections within the platform were made to ensure safe operation with the HV unit.

IMPORTANT: The power system must be checked by a certified electrician. It is NOT recommended to perform wiring of mains power, earthing as well as any of the power devices by an unauthorised person.

Once the mains power is connected, make sure the power is switched OFF.

1) Connect the positive and negative output of 48VDC.
2) Use terminal jumpers to distribute accordingly.
3) Connect the positive and negative output of 24VDC.
4) Use terminal jumpers to distribute accordingly.
5) Connect the positive and negative output of 12VDC.
6) Use terminal jumpers to distribute accordingly.

Follow ‘Power distribution diagram.pdf’ in supporting documents¹⁰ to connect input power to other electrical devices.

1) Connect 12VDC to Smoothieboard.
2) Connect 24VDC to the pressure regulator.
3) Connect 24VDC to the pressure sensor.
4) Connect 48VDC to the linear actuators.

¹⁰https://github.com/Lasonic/automated_mew_platform/blob/master/Electrical%20diagrams/Power%20distribution%20diagram.pdf

7. Safety

Timing: 1h

Materials: Non-contact magnetic switch, earth

Equipment: wire strippers

Critical: Make sure magnetic switches correctly toggle the electromagnetic relay on and off before connecting high voltage unit.

Non-contact magnetic switches are used along with the relays to make sure the high voltage is disconnected when any doors of the platform are open. This minimises the risk of a user getting shocked by the high voltage. For more details refer to the installation guide “non-contact magnetic switch manual.pdf” available in supporting material¹¹.

1) Connect magnetic switch#1 Pin 1(Brown) to 24VDC.
2) Connect magnetic switch#1 Pin 3(Blue) to GND.
3) Connect magnetic switch#1 Pin 7(Gray) to 24VDC.
4) Connect magnetic switch#1 Pin 4(Black) to magnetic switch#2 Pin 7(Gray).
5) Connect magnetic switch#2 Pin 4(Black) to relay input.
6) Connect relay output to GND.
7) Connect a diode1N4004 between magnetic switch#1 Pin 1(Brown) and Pin 4(Black)
8) Connect a diode1N4004 between magnetic switch#2 Pin 1(Brown) and Pin 4(Black)

¹¹https://github.com/Lasonic/automated_mew_platform/blob/master/Electrical%20diagrams/non-contac%20magnetic%20switch%20manual.pdf

8. Monitoring and illumination

Timing: 1h

Materials: USB3 cable, lens, camera, LED panel, 12VDC power supply, solder, 0.5mm² black and red cable, M5 screws and hammer nuts

Equipment: Soldering iron, M5 Allen key

Critical: Consider heat radiating from the LED at high current operation.

Basler Ace camera is connected with a computing PC via a USB3 cable.

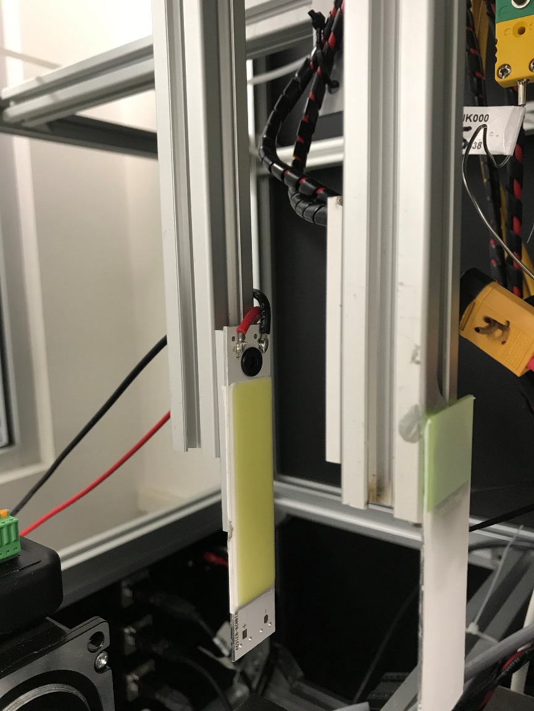
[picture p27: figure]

A 20x40mm LED panel was mounted on a 20x20 profile and powered with an external power source as shown in Figure 7.

Figure 7. LED panel was placed along the axis of the camera to create backlight illumination and obtain a silhouette of the fibre jet.

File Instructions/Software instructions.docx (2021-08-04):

Firmware and software instructions

Computing unit preparation

1) Install windows drivers for TTL-USB device by following the instructions in the Readme file. “PL2303_64bit_Installer.exe” executable file with the drivers is provided. Alternatively, it can be found online¹.
2) If you are using Windows version older than 10, follow the instructions² to install Smoothieboard drivers.
3) Download³ and install the latest Arduino IDE.
4) Download⁴ and install Python 3.
5) Download⁵ and install Pylon 6 Camera Software Suite. For operating systems other than Windows use Basler software search engine⁶.
6) Download Arduino libraries⁷ and save in the Arduino library folder.
7) Suggested Python editor: Spyder – The Scientific Python Development Environment. Follow online installation guide⁸ to install Spyder on the computing PC.

Arduino firmware initialisation

1) Open Arduino firmware sketch called “MEW digital platform 1.0”.
2) Make sure Arduino Due board and correct port are selected.
3) Upload the sketch.

Smoothieboard firmware initialisation

Smoothie is configured simply by editing a configuration file on its SD card. Essential temperature and linear actuators settings need to be configured in order to ensure correct Smoothieboard operation.

1) In configuration file, specify both temperature sensor to AD8495 amplifier by setting ‘temperature_control.hotend.sensor’ and ‘temperature_control.bed.sensor’ to ‘ad8495’.
2) Define the pin for each sensor. Set ‘temperature_control.hotend.ad8495_pin’ to ‘0.23’ and ‘temperature_control.bed.ad8495_pin’ to ‘0.24’.
3) If needed, adjust the temperature reading by adjusting the offset value of ‘temperature_control.hotend.ad8495_offset’ and ‘temperature_control.bed.ad8495_offset’.
4) Define correct steps per millimetre conversion by setting ‘alpha_steps_per_mm’, ‘beta_steps_per_mm’ and ‘gamma_steps_per_mm’ to 800.

Refer to online resources for more details on temperature⁹ and linear actuation¹⁰ configuration. Once the configuration is ready:

1) Upload “config” file to the SD card used with a Smoothieboard.
2) Reset Smoothieboard to implement the changes.

For more detailed information on how to configure Smoothieboard refer to the “Configuration file” section¹¹ of the online documentation.

Python user interface initialisation

Python UI was developed by modifying an existing code¹². Before running the main function “MEW digital platform UI.py”, open the function in Sypder (or another text editor) and make sure that the selected “COM” port corresponds to the port Arduino Due is connected to.

¹ http://www.prolific.com.tw/US/ShowProduct.aspx?p_id=225&pcid=41

² http://smoothieware.org/windows-drivers

³ https://www.arduino.cc/en/software

⁴ https://www.python.org/downloads/

⁵ https://www.baslerweb.com/en/sales-support/downloads/software-downloads/pylon-6-1-1-windows/

⁶ https://www.baslerweb.com/en/sales-support/downloads/software-downloads/

⁷https://github.com/Lasonic/automated_mew_platform/tree/master/Firmware_and_software/Arduino_libraries

⁸ https://docs.spyder-ide.org/current/installation.html

⁹ http://smoothieware.org/temperaturecontrol

¹⁰ http://smoothieware.org/stepper-motors

¹¹ http://smoothieware.org/configuring-smoothie

¹² https://gist.github.com/andySigler/80c60d3f7e4ba4a950200cccc6400ca1

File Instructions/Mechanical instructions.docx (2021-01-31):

Mechanical instructions

1. Linear actuators

Timing: 3h

Materials: As listed in the kit documentation

Equipment: M5 Allen key, spanners

Critical: Make sure the gantry plates are properly assembled to maximise stability of the moving components.

Assembly of the linear stages was completed according to the step-by-step instructions¹ provided by OpenBuilds. An assembled 3-axis linear actuator system is shown Figure 1:

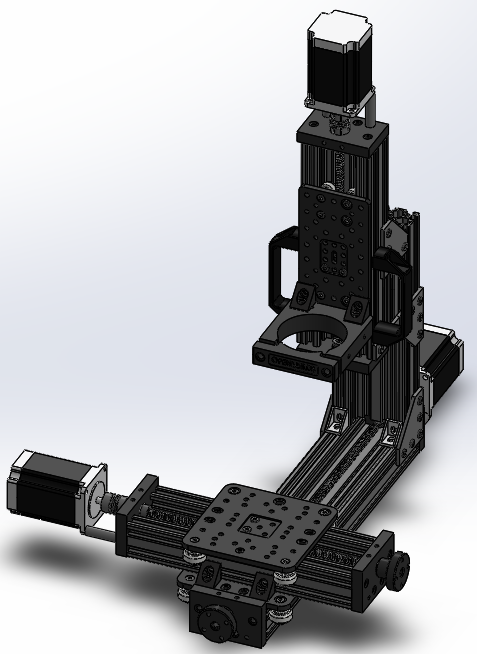
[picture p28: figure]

Figure 1. Finalised assembly of the 3-axis linear actuator.

¹ https://openbuilds.com/builds/openbuilds-minimill.5087/

2. Print bed

Timing: 0.5h

Materials: Gantry plate, Aluminium collector plate, screws (M5, M4), aluminium spacers.

Equipment: M4, M5 Allen keys.

Critical: Screws used to fix the Aluminium collector plate need to be countersunk.

Print bed consist of a gantry plate (Figure 2/A) and an Aluminium collector plate (Figure 2/B). It was designed to provide a simple collection system of MEW fibres, while offering flexibility of the design to allow for potential print bed upgrades such as different collector geometry.

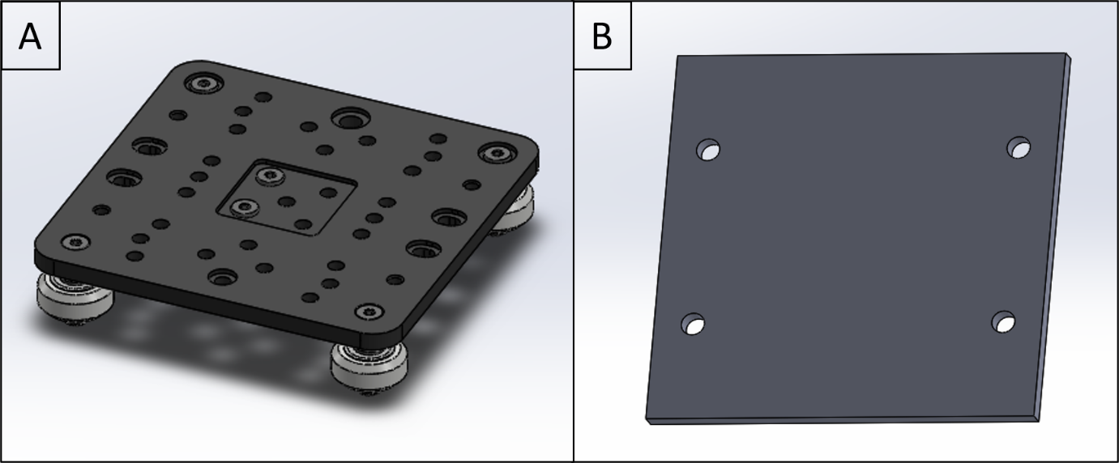
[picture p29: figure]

Figure 2. Print bed system consisting of (A) gantry cart and (B) Aluminium collector plate.

1) Feed four M5 screws through the dedicated holes in the Aluminium collector plate.
2) Place Aluminium spacers around the screws.
3) Mount the Aluminium collector plate onto the gantry plate using the threaded screw holes in the gantry plate.
3. Printhead

Timing: 1h

Materials: Flat head screwdriver, Kapton tape

Critical: Make sure the ring thermocouple is fed all the way to the bottom so it is in contact with the ring heater. Similarly, make sure the syringe thermocouple is fed half-way to the bottom through the hole.

The printhead provides storage for material used during printing process while maintaining desired material temperature via heating elements.

1) Fit syringe heater into the hollow cavity of the printhead.
2) Fit ring heater into the bottom part of the printhead.
3) Apply 2 layer of Kapton tape onto the outer part of the ring heater to protect the heating element from high voltage.
4) Fit the brass plate into the additional part of the printhead.
5) Connect the high voltage wire to the brass ring.
6) Connect both parts of the printhead together using Nylon screws.
7) Feed a K-type thermocouple through the hole as shown in Figure X.
8) Feed a K-type thermocouple half-way through the hole as shown in Figure X.
9) Place a syringe inside the printhead so that the nozzle pokes through a hole in the ring heater outside the printhead.
10) Bend the wiring and use a clamp arrangement to lock the syringe insider the printhead and keep the electrical connections secured.

Take actual pictures of the printhead assembly.

4. Framework

Timing: 3h

Materials: Corner brackets, 30x30 aluminium profiles, 20x20 aluminium profiles, 20x80 aluminium profiles, M5 hammer nuts and M6 nuts, latching magnets, door handles, laser cut parts.

Equipment: M6 and M5 Allen keys, spirit level.

Critical: Make sure that corner brackets are flash with the adjacent panels to achieve solid and robust construction.

Framework consists of 30x30mm and 20x20 aluminium extrusion profiles connected together using corner brackets. Top section consists of sensors and actuators mounted directly to the framework, while the bottom section consists of electrical components assembled on an Aluminium plate and two gantry plates.

1) Connect the base of a frame using six 850mm and two 680mm 30x30 aluminium profiles (Figure1/A).
2) Follow OpenBuilds instructions¹ to assemble two gantry carts.
3) Use four 80x20 profiles to fit two gantry carts from step 2)
4) Use a 30x30 profile and to complete the base of the frame (Figure1/B).
5) Attach nine 30x30 profiles (Figure1/C).
6) Attach linear stages system developed in 1).
7) Attach four 20x20 profiles (Figure1/D).
8) Construct and attach vision system support. INCLUDING RAIL FOR LED
9) Use eight 30x30 profiles, hinges and door handles to construct a pair of doors.
10) Attach the door to the frame (Figure1/E).
11) Use four 30x30x profiles to finish the top part for the framework (Figure1/F).
12) Use an acrylic panel, hinges and a door handle to construct electrical door.
13) Attach four pairs of magnets to construct latches for the electrical and main door.
14) Attach silicone bumpers on the inside of the electrical door (OPTIONAL)

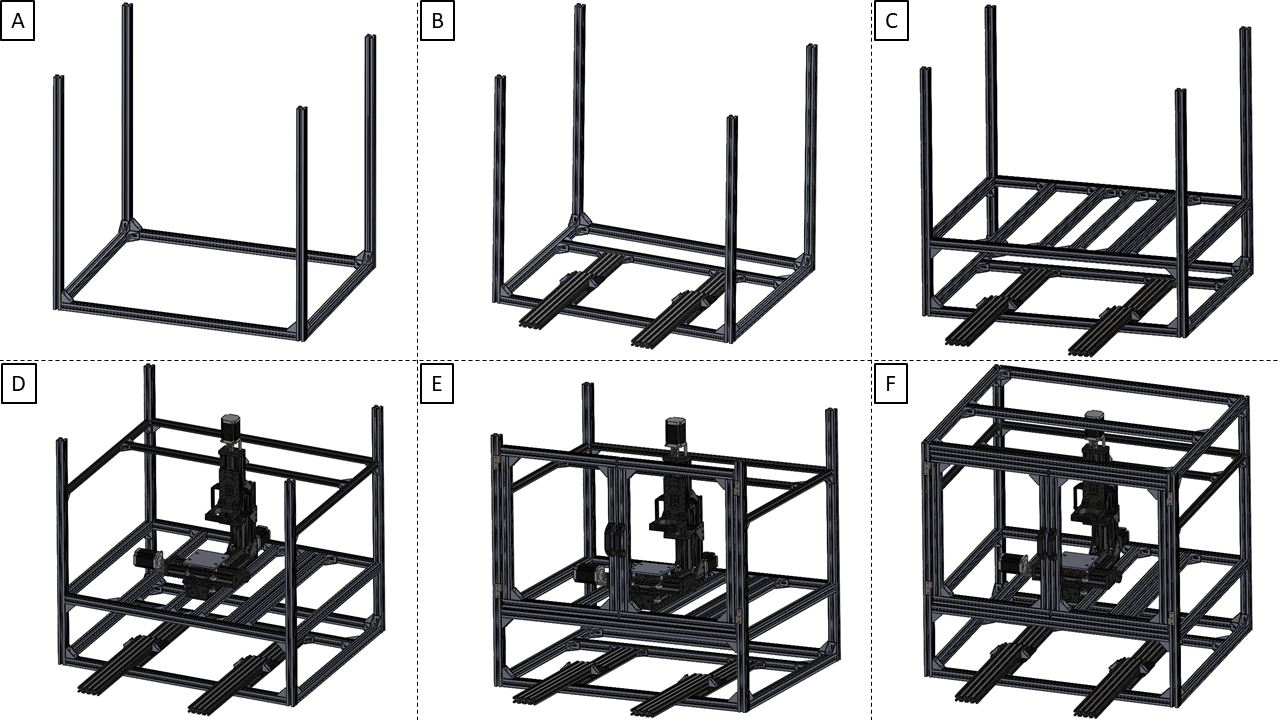
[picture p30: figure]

Figure 3. Framework assembly process includes assembly of (A) a base frame with (B) sliding gantry system of (C) electrical section, (D) printing section with linear actuators, (E) printing section access door and (F) complete framework.

5. Final step

Timing: 3h

Materials: Printhead, printhead clamp, pressure regulator, pressure sensor, high voltage unit, thermocouple and thermocouple connectors, camera, lens, lens clamp, non-contact magnetic switches, laser cut acrylic panels.

Equipment: M5 Allen key,

Critical:

In the last step we finalise mechanical assembly by mounting a print bed, printhead, electrical components and acrylic panels.

1) Place the printhead in the dedicated head holder.
2) Attach the printhead using a custom-made replacement clamp.
3) Attach pressure regulator.
4) Attach pressure sensor.
5) Attach high voltage power supply.
6) Attach thermocouple connections.
7) Mount monitoring system.
8) Attach a non-contact safety switch on both doors.
9) Attach top acrylic panels.
10) Attach back acrylic panels.
11) Attach left side acrylic panels.
12) Attach right size acrylic panels.
13) Attach front door acrylic panels.
14) Attach front electrical drawer acrylic panels.

Missing acrylic panels

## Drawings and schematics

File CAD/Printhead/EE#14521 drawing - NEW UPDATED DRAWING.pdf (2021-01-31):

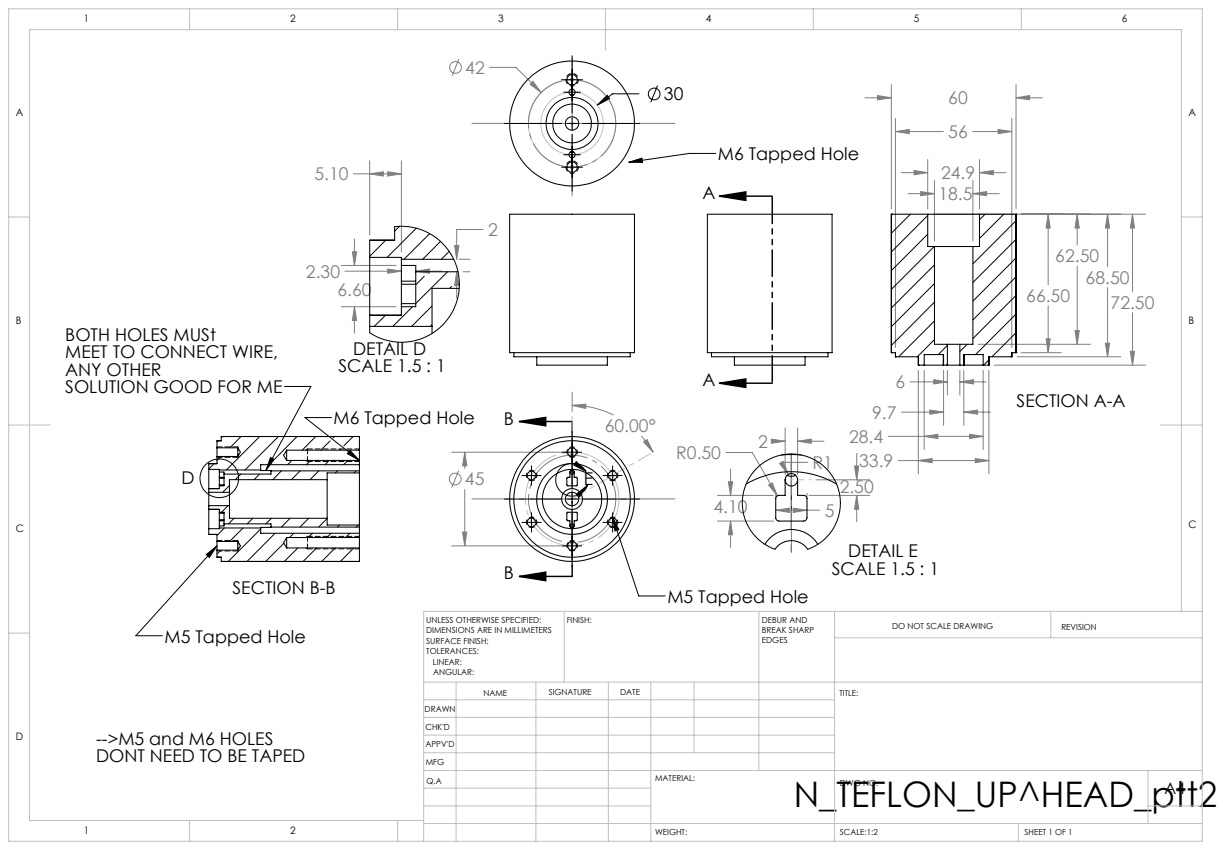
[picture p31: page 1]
M6 Tapped Hole; M5 Tapped Hole; SECTION A-A; SECTION B-B; DETAIL D SCALE 1.5 : 1; DETAIL E SCALE 1.5 : 1; FINISH:; DEBUR AND; BREAK SHARP; DO NOT SCALE DRAWING; REVISION; SCALE:1:2; SHEET 1 OF 1

BOTH HOLES MUSt
MEET TO CONNECT WIRE,
ANY OTHER
SOLUTION GOOD FOR ME

UNLESS OTHERWISE SPECIFIED:
DIMENSIONS ARE IN MILLIMETERS
SURFACE FINISH:
TOLERANCES:
LINEAR:
ANGULAR:

NAME | SIGNATURE | DATE | | | | TITLE:

DRAWN
CHK'D
APPV'D
MFG
Q.A | | | | MATERIAL: | DWG NO. | A4

-->M5 and M6 HOLES
DONT NEED TO BE TAPED

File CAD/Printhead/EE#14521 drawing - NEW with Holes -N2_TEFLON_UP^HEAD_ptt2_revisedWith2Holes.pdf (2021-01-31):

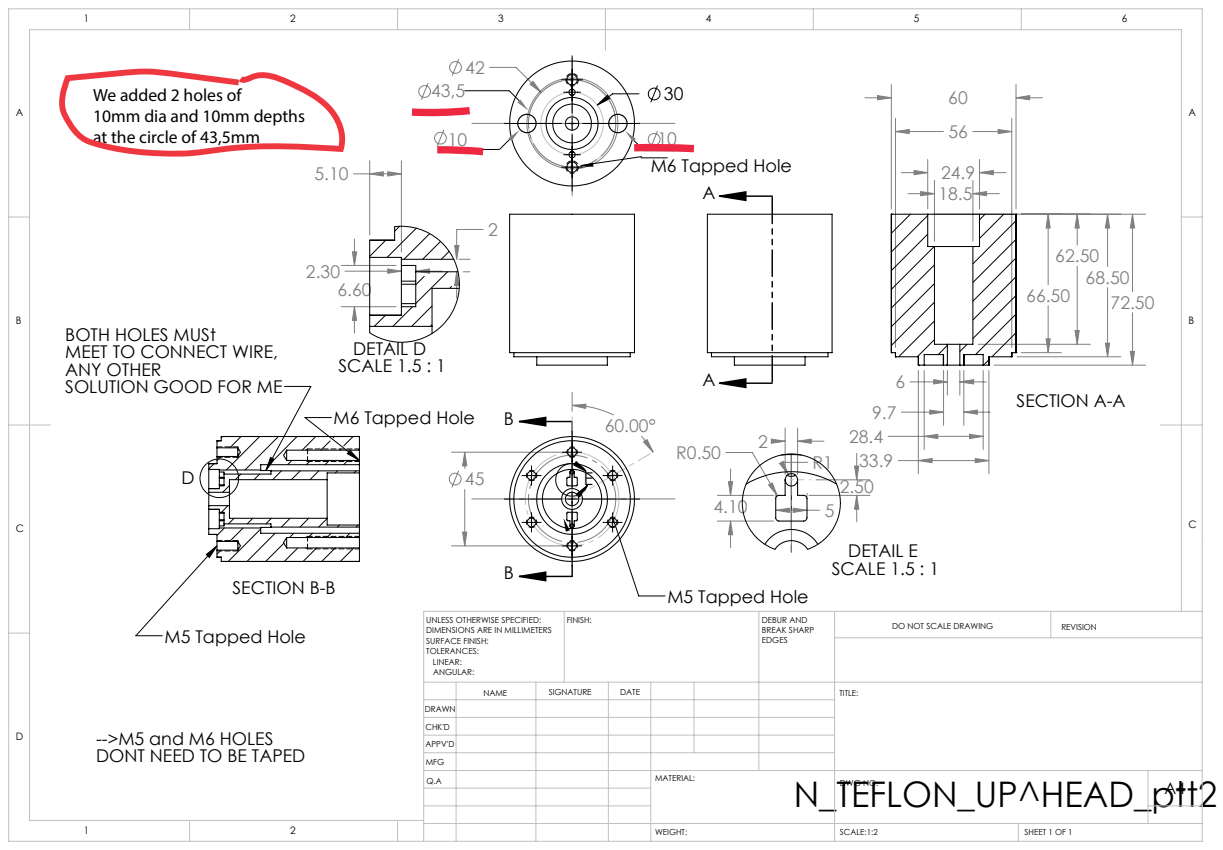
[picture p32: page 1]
M6 Tapped Hole; M5 Tapped Hole; SECTION A-A; SECTION B-B; DETAIL D SCALE 1.5 : 1; DETAIL E SCALE 1.5 : 1; FINISH:; DEBUR AND; BREAK SHARP EDGES; DO NOT SCALE DRAWING; REVISION; SCALE:1:2; SHEET 1 OF 1; WEIGHT:; N_TEFLON_UP^HEAD_ptt2

We added 2 holes of
10mm dia and 10mm depths
at the circle of 43,5mm

BOTH HOLES MUSt
MEET TO CONNECT WIRE,
ANY OTHER
SOLUTION GOOD FOR ME

UNLESS OTHERWISE SPECIFIED:
DIMENSIONS ARE IN MILLIMETERS
SURFACE FINISH:
TOLERANCES:
LINEAR:
ANGULAR:

NAME | SIGNATURE | DATE | | | | TITLE:

DRAWN
CHK'D
APPV'D
MFG
Q.A | | | | MATERIAL: | DWG NO. | A4

-->M5 and M6 HOLES
DONT NEED TO BE TAPED

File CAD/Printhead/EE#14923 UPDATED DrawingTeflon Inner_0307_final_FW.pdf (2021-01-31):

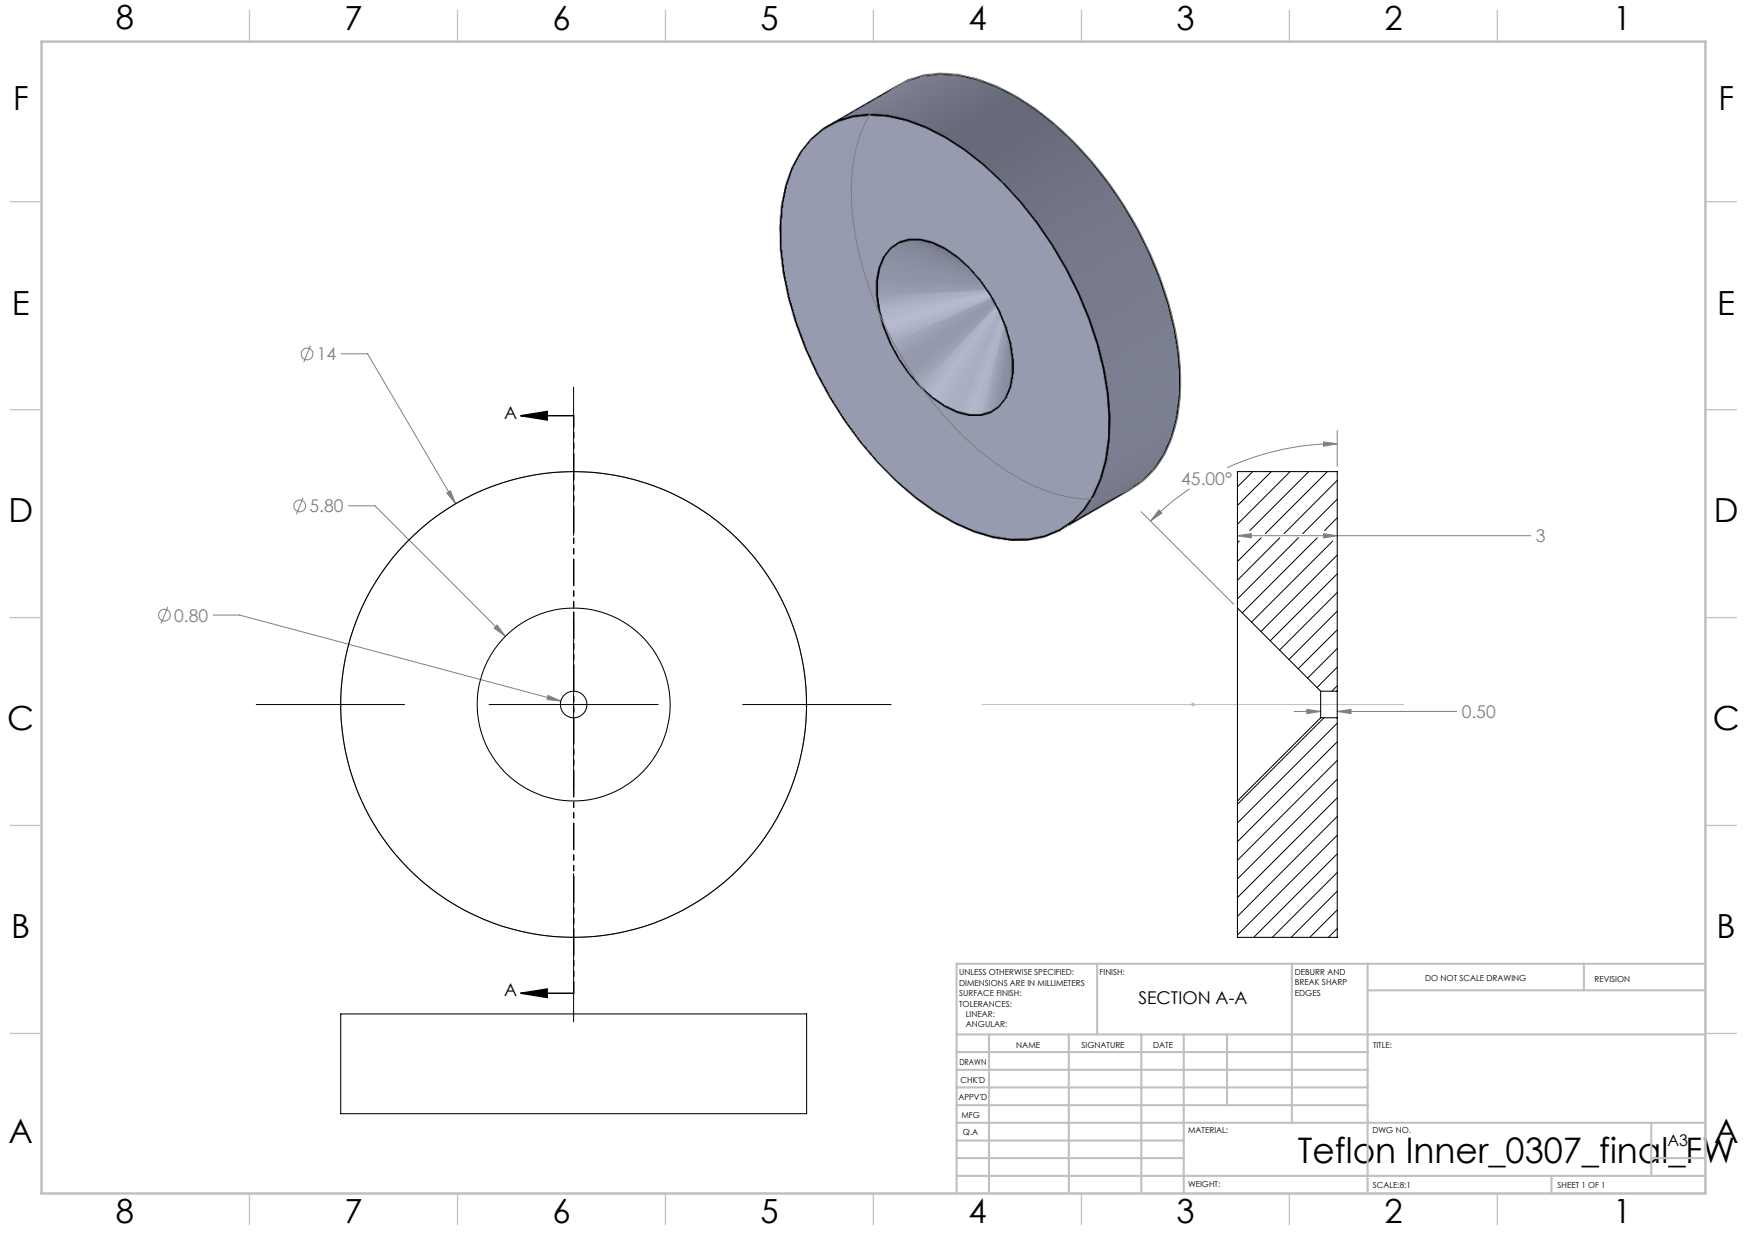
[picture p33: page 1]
SECTION A-A; FINISH:; DEBURR AND; BREAK SHARP; DO NOT SCALE DRAWING; REVISION; SCALE:8:1; SHEET 1 OF 1; Teflon Inner_0307_final_FW

UNLESS OTHERWISE SPECIFIED:
DIMENSIONS ARE IN MILLIMETERS
SURFACE FINISH:
TOLERANCES:
LINEAR:
ANGULAR:

NAME | SIGNATURE | DATE | | | | TITLE:

DRAWN
CHK'D
APPV'D
MFG
Q.A | | | | MATERIAL: | DWG NO. | A3

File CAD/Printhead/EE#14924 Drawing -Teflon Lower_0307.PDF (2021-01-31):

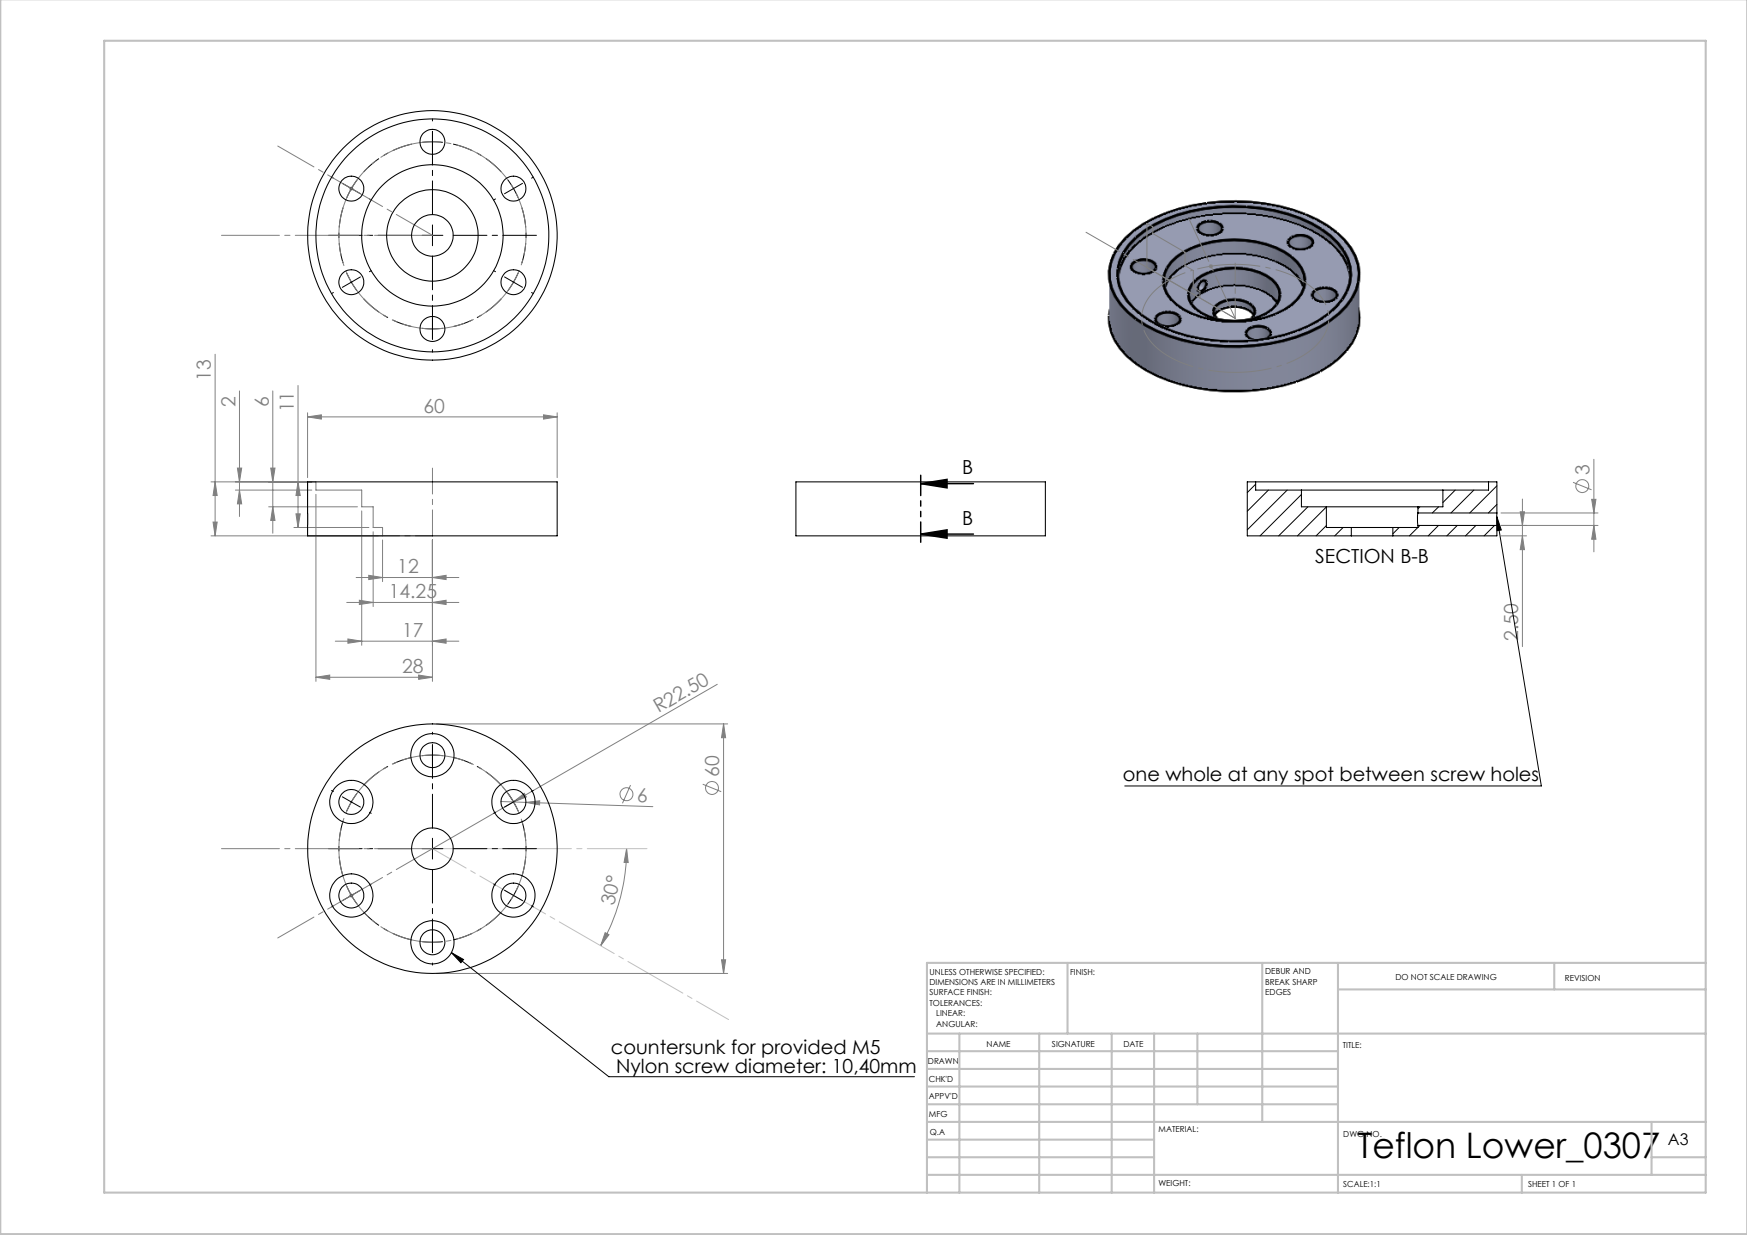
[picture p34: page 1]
SECTION B-B; SCALE:1:1; SHEET 1 OF 1; DO NOT SCALE DRAWING; REVISION; DEBUR AND BREAK SHARP; UNLESS OTHERWISE SPECIFIED:; FINISH:

one whole at any spot between screw holes

DIMENSIONS ARE IN MILLIMETERS
SURFACE FINISH:
TOLERANCES:
LINEAR:
ANGULAR:

countersunk for provided M5
Nylon screw diameter: 10,40mm

NAME | SIGNATURE | DATE | | | | TITLE:
Q.A | | | | MATERIAL: | Teflon Lower_0307 WEIGHT: DWG NO. | A3

DRAWN
CHK'D
APPV'D
MFG

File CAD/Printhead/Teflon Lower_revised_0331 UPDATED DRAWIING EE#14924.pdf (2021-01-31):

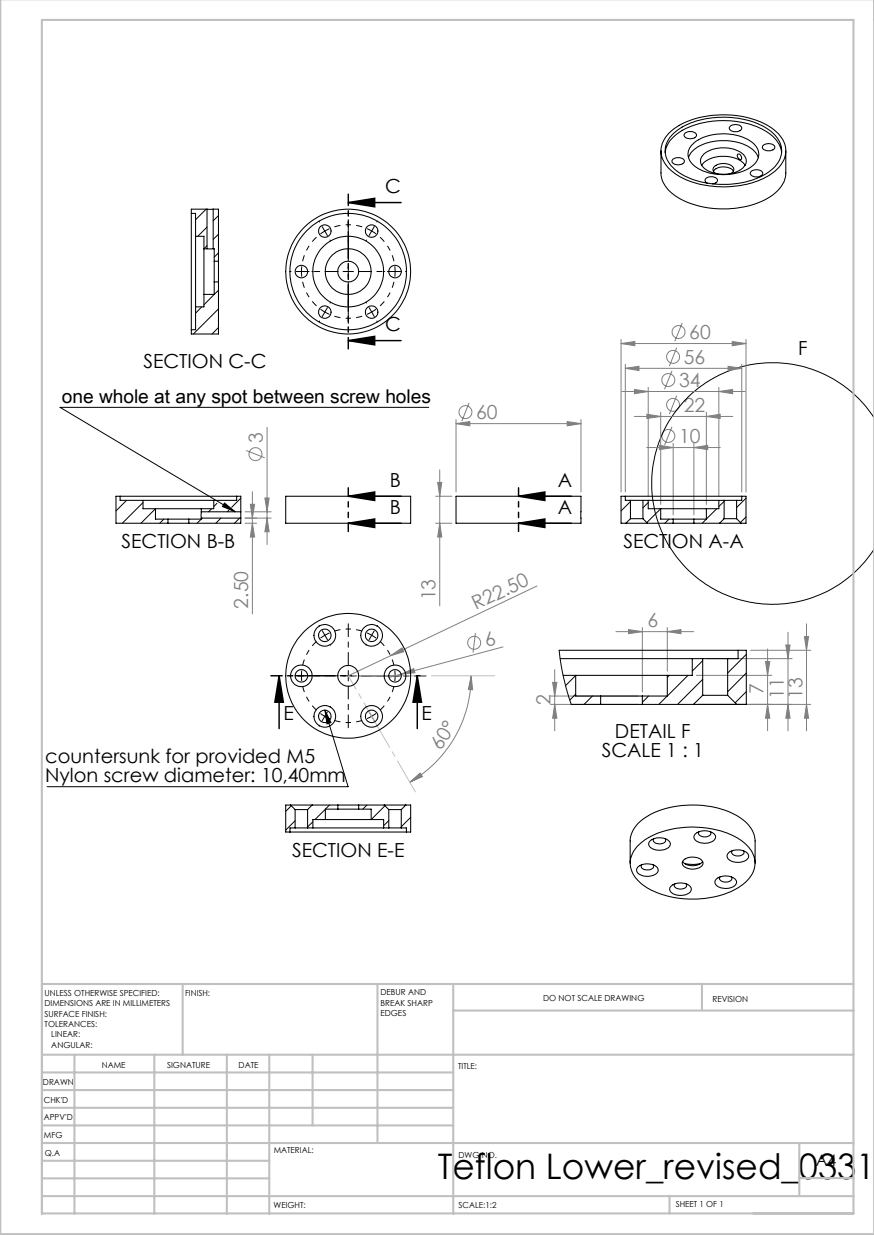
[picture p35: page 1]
SECTION A-A; SECTION B-B; SECTION E-E; DETAIL F SCALE 1 : 1; SCALE:1:2; SHEET 1 OF 1; DO NOT SCALE DRAWING; REVISION; DEBUR AND BREAK SHARP; UNLESS OTHERWISE SPECIFIED:; FINISH:

SECTION C-C
one whole at any spot between screw holes

countersunk for provided M5
Nylon screw diameter: 10,40mm

DIMENSIONS ARE IN MILLIMETERS
SURFACE FINISH:
TOLERANCES:
LINEAR:
ANGULAR:

NAME | SIGNATURE | DATE | | | | TITLE:
Q.A | | | | Teflon Lower_revised_0331 WEIGHT: MATERIAL: | DWG NO. | A4

DRAWN
CHK'D
APPV'D
MFG

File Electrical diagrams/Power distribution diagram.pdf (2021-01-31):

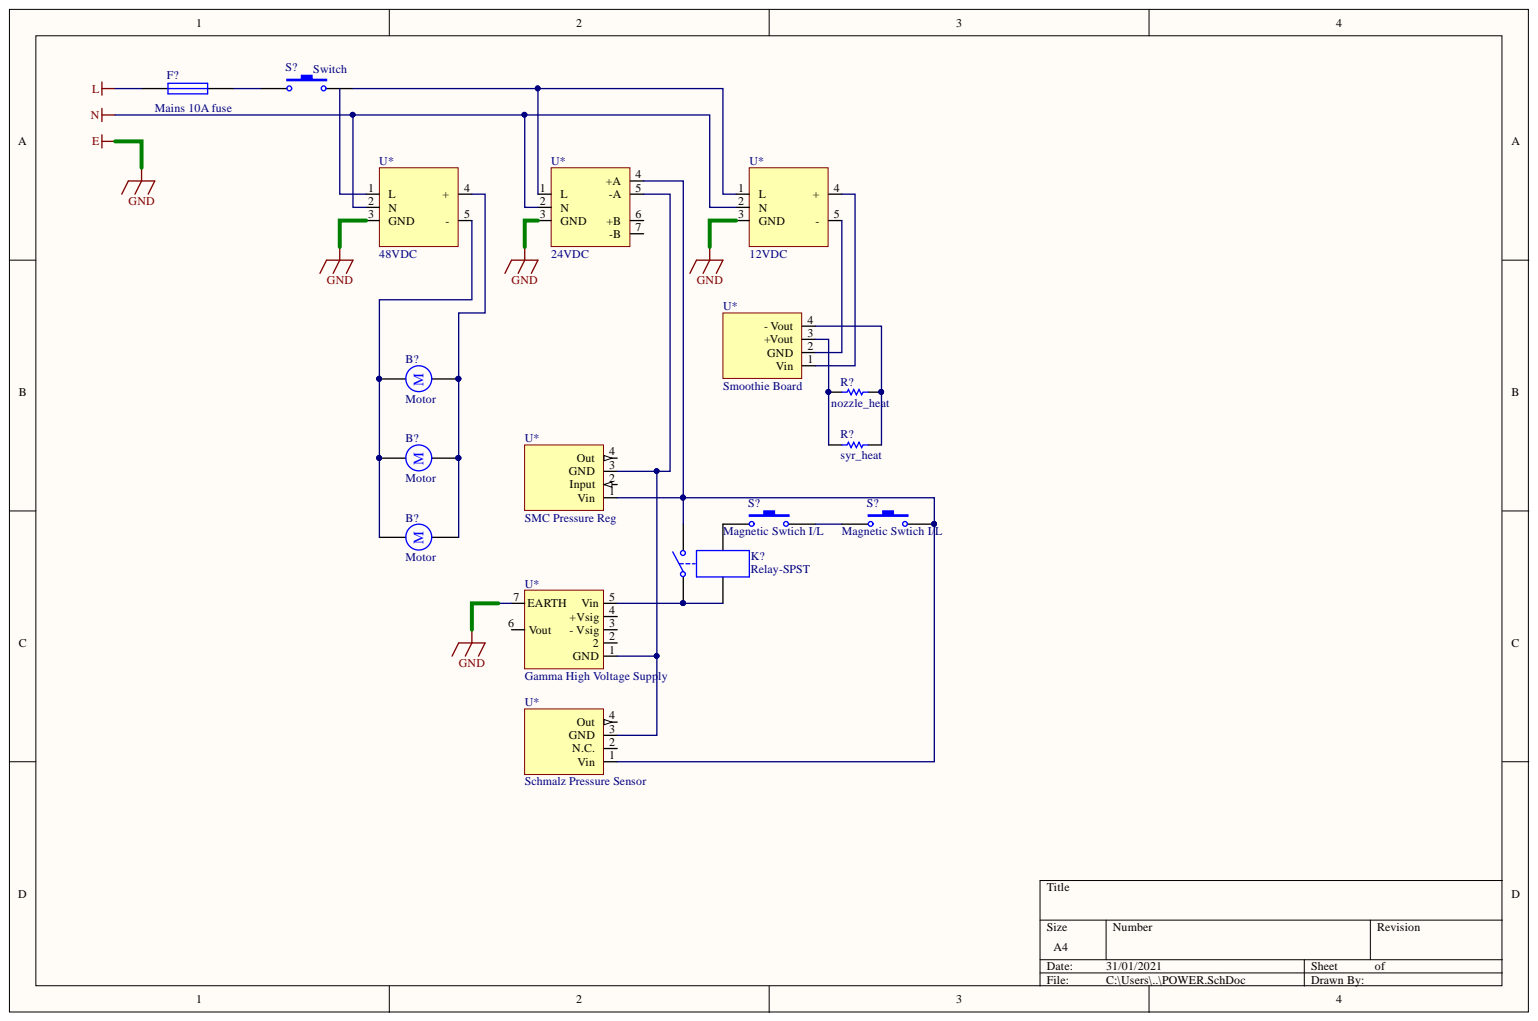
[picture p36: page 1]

Gamma High Voltage Supply

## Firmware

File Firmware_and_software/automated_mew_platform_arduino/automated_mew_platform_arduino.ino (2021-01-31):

#include <math.h>
#include <Wire.h>                                                                 // I2C library
#include <SPI.h>                                                                  // SPI library  
//#include <PID_v1.h>
#include <ctype.h>
#include <string.h>
#include <Adafruit_MCP4725.h>                                                     // DAC IC library


Adafruit_MCP4725 dac_hv;                                                          // Define hv DAC
Adafruit_MCP4725 dac_pres;                                                        // Define pressure DAC


int pressure_set_pin = DAC0;
int voltage_set_pin = DAC1;

int pressure_read_pin = A0;
int voltage_read_pin = A1;
int current_read_pin = A2;
int ambientTemp_read_pin = A3;
int hum_read_pin = A4;


/// SET INPUT PARAMETERRS ///

//Data_in already decoded and ready to use. Arduino Due supports 2 DAC. Max resolution 12bit. Range: 0.55-2.7V.
//Amplification of gain = 3 is used.

void set_pressure(int input_value) {                                              //Set voltage. Maximum pressure value 4Bar.
  int new_pressure = input_value - 100000;                                        //Decode to get the pressure value in kPa
  if (new_pressure > 400) {                                                       //Make sure the maximum pressure does not exceed 4bar
    new_pressure = 400;
  }
  else if (new_pressure < 0) {                                                    //Minimum pressure is 0.
    new_pressure = 0;
  }
  else {
    int new_pressure_to_dac = round(4095* new_pressure * 0.8 / 400);
    dac_pres.setVoltage(new_pressure_to_dac, false);                              //Set analog output pressure.
    //Serial.println(new_pressure_to_dac);
    //Serial.println("ok");
    //analogWrite(pressure_set_pin,4096*(new_pressure/400));                      //Convert the input_value to the pressure scale.
  }
}

void set_voltage(int input_value) {
  int new_voltage = input_value - 200000;                                         //Decode to get the pressuse value in volts.
  if (new_voltage > 25000) {                                                      //Set voltage. Maximum voltage value 25kV.
    new_voltage = 25000;
  }
  else if (new_voltage < 0) {
    new_voltage = 0;
  }
  else {
    int new_voltage_to_dac = 4095 * new_voltage / 19000;                          //Set analog output voltage. Number given in VOLTS.
    dac_hv.setVoltage(new_voltage_to_dac, false);                                 //Convert the input_value to the voltage scale.
    //Serial.println(new_voltage_to_dac);
    //Serial.println("ok");
    //analogWrite(voltage_set_pin,4096*(input_value/25000));
  }
}

/// READ INPUT PARAMETERRS ///
int read_pressure(int data_in = analogRead(A0)) {                                 //Read current pressure. Data_in range is converted from 0-3.3V to 0-4096.
  int result = round(data_in * 330 * 1.58 / 4095);                                        //Convert from analog voltage to kPa value. Use scalar of 1.58 as a correcting factor.
  
  return result;
}

int read_voltage(int data_in = analogRead(A1)) {                                  //Read current voltage. Data_in range is converted from 0-2.5V to 0-4096.
  int result = data_in * 33330 / 3795;                                            //Convert from analog voltage to the actual voltage. Use a value of 3795 (instead of 4095) as a correcting factor.
  return result;
}

int read_current(int data_in = analogRead(A2)) {                                  //Read current voltage. Data_in range is converted from 0-2.5V to 0-4096.
  int result = data_in * 250 / 3102;                                              //Convert from analog voltage to mA.
  return result;
}
void read_ambientTemp() {
}
void read_hum() {
}

void setup() {
  //SERIAL INIT
  Serial.begin(115200);                                                           //Communicate with MATLAB via TTL to USB (COM14)
  //Serial1.begin(115200);
  Serial1.begin(115200);                                                          //Communicate with Python (COM6)
  //DUE ADC RESOLUTION
  Serial2.begin(115200);
  analogReadResolution(12);

  //DUE/DAC RESOLUTION
  analogWriteResolution(12);

  // ADAFRUID IC DAC HV setup
  dac_hv.begin(0x62);                                                             // deafauly ADAFRUIT IC DAC address is 0x62. IF A0 is connected to VCC
  // the address is 0x63
  // ADAFRUIT IC DAC PRESSURE setup
  dac_pres.begin(0x63);

  //PRESSURE OUTPUT INIT
  pinMode(DAC0, OUTPUT);

  //VOLTAGE OUTPUT INIT
  pinMode(DAC1, OUTPUT);

  //PRESSURE INPUT INIT
  pinMode(pressure_read_pin, INPUT);

  //VOLTAGE INPUT INIT
  pinMode(voltage_read_pin, INPUT);

  //CURRENT INPUT INIT
  pinMode(current_read_pin, INPUT);

  //AMBIENT TEMP INPUT INIT
  pinMode(ambientTemp_read_pin, INPUT);

  //HUMIDITY INPUT INIT
  pinMode(hum_read_pin, INPUT);

  dac_hv.setVoltage(1, false);   //HV
  dac_pres.setVoltage(1, false);   //AP
}

void loop() {
  //dac_hv.setVoltage(4095,false);
  ///// PYTHON USER INPUT /////
  // This will only be execured if there is incoming request from the user
  //delay(50);
  //Serial1.println(round(analogRead(A0)*1.58*330/4095));
  //Serial1.print(" ");

  if (Serial.available() > 0) {                                                  //Chekc if data is received from Python(user). This allows user
    //Serial1.print("test1");                                                         //to change the parameters.
    int python_data_in = Serial.parseInt();                                      //Read integer
    if (python_data_in > 100000 && python_data_in < 200000) {                     //If true, data_in is new pressure to set. Number given as 100;000 + desired pressure(in kPa).
      //Serial1.println(python_data_in);
      //Serial.println(python_data_in);
      set_pressure(python_data_in);
    }
    else if (python_data_in > 200000 && python_data_in < 300000) {                //If true, data_in is new voltage to set. Number given as 200'000 + desired voltage(in Volts).
      //Serial1.println(python_data_in);
      //Serial.println(python_data_in);
      set_voltage(python_data_in);
    }
    /*
      else if (python_data_in > 300000 && python_data_in < 400000){                 //If true, set this temperature on SMOOTHIEBOARD
      }
      else if (python_data_in > 400000 && python_data_in < 500000){                 //If true, set this collection speed on SMOOTHIEBOARD
      }
      else if (python_data_in > 500000 && python_data_in < 600000){                 //If true, set this collection speed on SMOOTHIEBOARD
      }
    */
  }

  ///// MATLAB program input /////
  // This will only be execured if MATLAB request data or parameter change

  if (Serial1.available() > 0) {
    //Check data requests first
    //String MATLAB_data_in_string = Serial.readStringUntil('\n');                //Check if data is received from MATLAB. This allows MATLAB to
    int MATLAB_data_in_int = Serial1.parseInt();                                  //automaticall change the input parameters
    Serial.println(MATLAB_data_in_int);
    if (MATLAB_data_in_int == 100) {                                              //If pressure is requested,send current pressure value.
      int current_pressure = read_pressure();
      Serial1.println(current_pressure);
      Serial1.println("ok");      
    }
    else if (MATLAB_data_in_int == 200) {                                         //If voltage is requested, send current voltage value.
      int current_voltage = read_voltage();
      // Serial1.println(current_voltage);
      Serial1.println(current_voltage);
      Serial1.println("ok");
    }
    else if (MATLAB_data_in_int == 300) {                                         //If current is requested, send current current value.
      int current_current = read_current();
      Serial1.println(current_current);
      Serial1.println("ok");
    }
    else if (MATLAB_data_in_int == 400) {                                         //If ambient temperature is requested, send current
      int current_amb_temp = 25;                                                  //ambient temperature value.
      Serial1.println(current_amb_temp);
      Serial1.println("ok");
    }
    else if (MATLAB_data_in_int == 500) {                                         //If humidity is requested, send current humidity value.
      int current_hum = 60;
      Serial1.println(current_hum);
      Serial1.println("ok");
    }
    //If no data is requested, check parameters need to be set
    else {
      //Serial1.println("test bad");
      if (MATLAB_data_in_int > 100000 && MATLAB_data_in_int < 200000) {           //Check if the encoded value is pressure.
        set_pressure(MATLAB_data_in_int);                                         //Set the new pressure value.
        //Serial1.println(MATLAB_data_in_int);
      }
      else if (MATLAB_data_in_int > 200000 && MATLAB_data_in_int < 300000) {
        set_voltage(MATLAB_data_in_int);
        //Serial1.println(MATLAB_data_in_int);
      }
    }
  }
}

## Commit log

2021-01-31 Design files
    [12VDC PSU.SLDPRT, 23GP_final.SLDPRT, 24VDC & 5VDC PSU.SLDPRT, 24VDC PSU + mains adapter.SLDPRT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]
2021-02-01 CAD changes and electrical updates
    [Arduino Shield v1.3.pcbdoc, BOM_automated_MEW_platform.xlsx]
2021-02-04 Upload 04.02.2021
    [BOM_automated_MEW_platform.xlsx, Inner_centre_left_acrylic.SLDPRT, Inner_centre_right_acrylic.SLDPRT, Inner_left_acrylic.SLDPRT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]
2021-02-22 22.02.21
    22.02.21 commit
    [Aluminum_plate_electronics.SLDPRT, BOM_automated_MEW_platform.xlsx, Pressure support bracket.SLDASM, Printgeah clamp.SLDPRT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]
2021-06-25 CAD printhead corrections
    [Printhead_top_part.SLDPRT, Syringe_top_clamp.SLDPRT, TUBE_TOP.SLDPRT, head_1103.SLDASM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]
2021-07-03 CAD electronics plate corrections
    [Aluminum_plate_electronics_final.SLDPRT]
2021-08-03 Update BOM_automated_MEW_platform.xlsx
    BoM update
    [BOM_automated_MEW_platform.xlsx]
2021-08-04 Final updates
    [Side_long.DWG, Side_long.SLDPRT, Side_short.DWG, Side_short.SLDPRT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]
